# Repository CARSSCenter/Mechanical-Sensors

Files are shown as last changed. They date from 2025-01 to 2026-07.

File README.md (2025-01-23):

# Mechanical-Sensors
Sensors for mechanical biomarkers designed to interface with the OpenNerve platform

# About
The capacitive strain sensor is manufactured using silicone rubber and a novel wrinkled Parylene C process for increased gauge factor.


The temperature sensor is manufactured from gold on a polyimide thin-film substrate.


# Disclaimer
The contents of this repository are subject to revision. No representation or warranty, express or implied, is provided in relation to the accuracy, correctness, completeness, or reliability of the information, opinions, or conclusions expressed in this repository.

The contents of this repository (the “Materials”) are experimental in nature and should be used with prudence and appropriate caution. Any use is voluntary and at your own risk.

The Materials are made available “as is” by USC (the University of Southern California and its trustees, directors, officers, employees, faculty, students, agents, affiliated organizations and their insurance carriers, if any), its collaborators Med-Ally LLC and Medipace Inc., and any other contributors to this repository (collectively, “Providers”). Providers expressly disclaim all warranties, express or implied, arising in connection with the Materials, or arising out of a course of performance, dealing, or trade usage, including, without limitation, any warranties of title, noninfringement, merchantability, or fitness for a particular purpose.

Any user of the Materials agrees to forever indemnify, defend, and hold harmless Providers from and against, and to waive any and all claims against Providers for any and all claims, suits, demands, liability, loss or damage whatsoever, including attorneys' fees, whether direct or consequential, on account of any loss, injury, death or damage to any person or (including without limitation all agents and employees of Providers and all property owned by, leased to or used by either Providers) or on account of any loss or damages to business or reputations or privacy of any persons, arising in whole or in part in any way from use of the Materials or in any way connected therewith or in any way related thereto.

The Materials, any related materials, and all intellectual property therein, are owned by Providers.

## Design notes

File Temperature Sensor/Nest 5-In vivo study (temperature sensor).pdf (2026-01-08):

## In Vivo Study (Rat)

The temperature sensor and commercial reference were fixed to the left thigh muscle of the rat. We recorded 6 sets of data at intervals of about 1 min, and the results showed that the difference between the temperature sensor and the commercial reference was always within 0.2 °C. The resolution of our temperature sensor was within 0.05 °C, meanwhile, there was no obvious noise found when working in vivo. Therefore, experiments in vitro and in vivo have reached similar conclusions: the temperature sensor has the characteristics of high accuracy and high resolution. The temperature sensor is suitable for implantable tissue/organ temperature measurement for various applications.

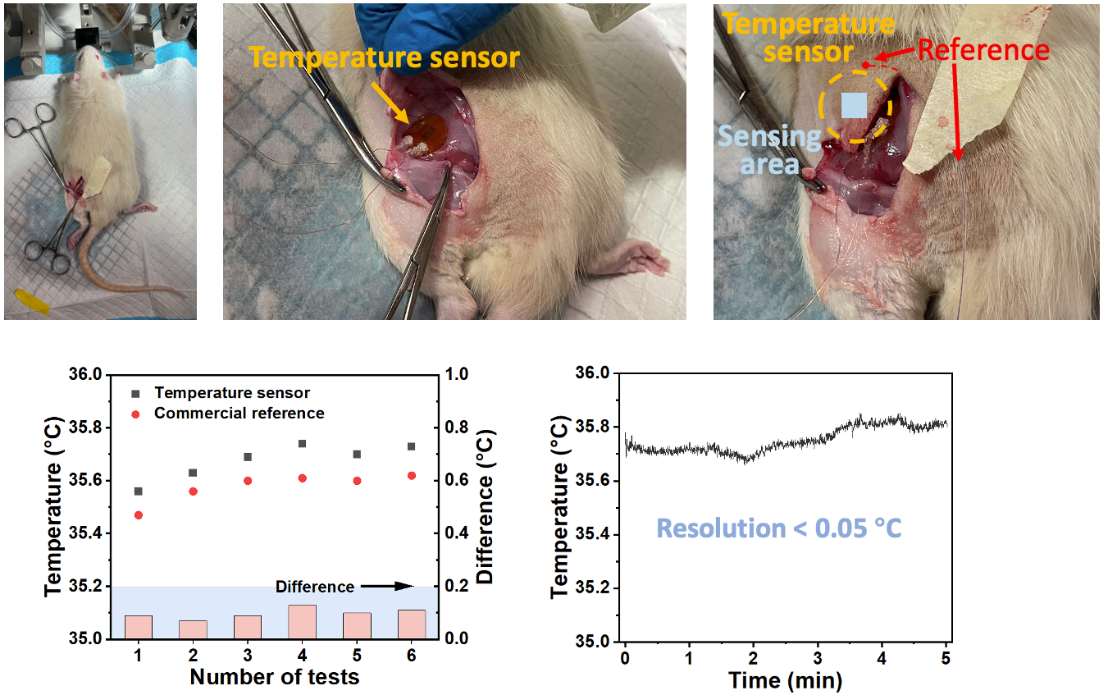
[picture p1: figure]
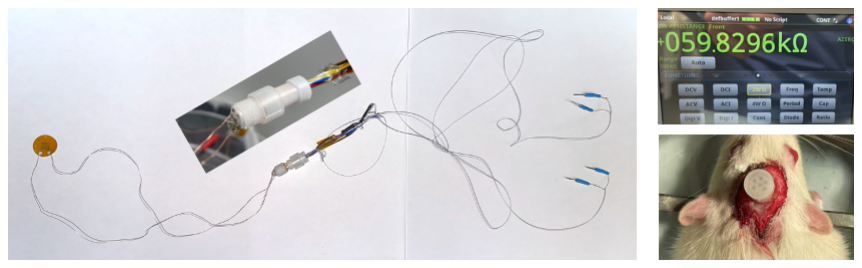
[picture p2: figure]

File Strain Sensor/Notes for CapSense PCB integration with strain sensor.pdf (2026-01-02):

# Stretchable capacitive strain sensor

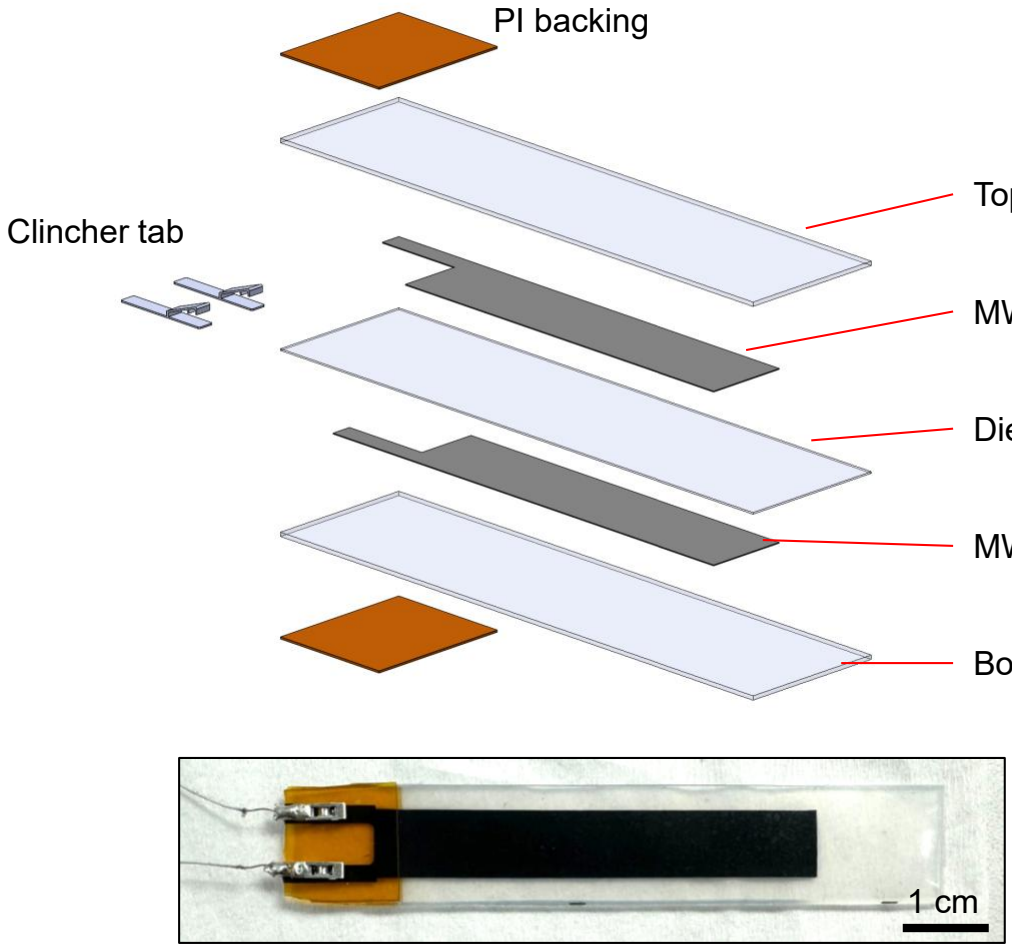
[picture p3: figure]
PI backing; Clincher tab

Custom strain sensor: spray-coated multiwall carbon nanotubes (MWCNTs) on Ecoflex

MWCNT

MWCNT

Top Ecoflex

Dielectric layer

Bottom Ecoflex

# Method 4: using single PI connector at the center of the sensor

Step 1: blade coat Ecoflex on a glass substrate. Next, spray coat the first CNT layer. Then, cover the contact pad with a film or tape. After that, blade coat the middle Ecoflex layer.

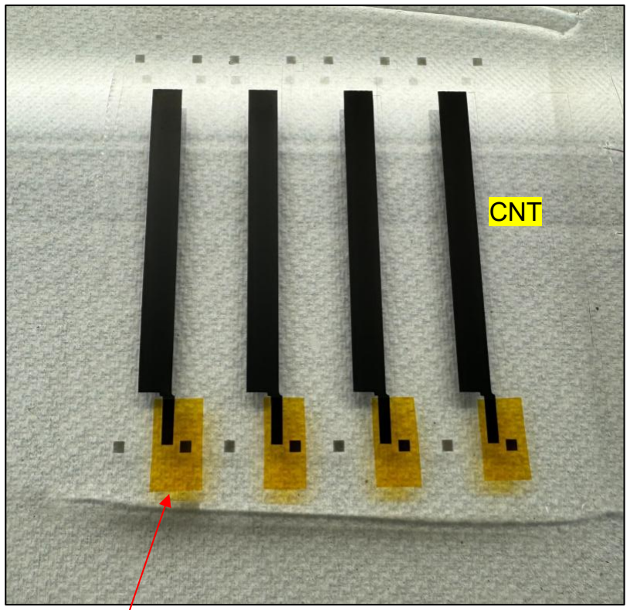
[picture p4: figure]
CNT
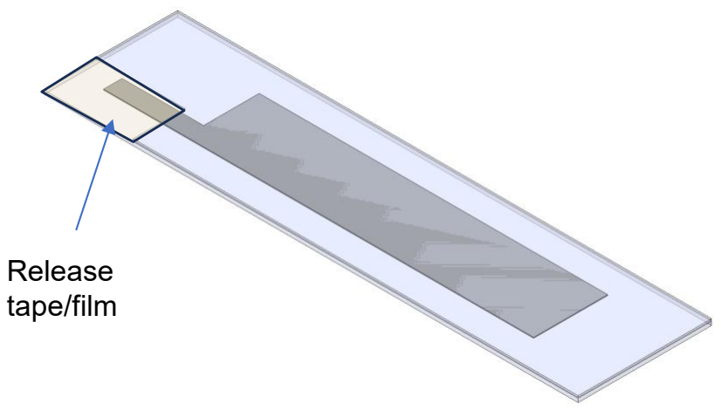
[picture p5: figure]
Release tape/film

Release
tape/film

# sensor

Step 2: remove the tape to expose the contact pad. Then, spray coat the second CNT Layer

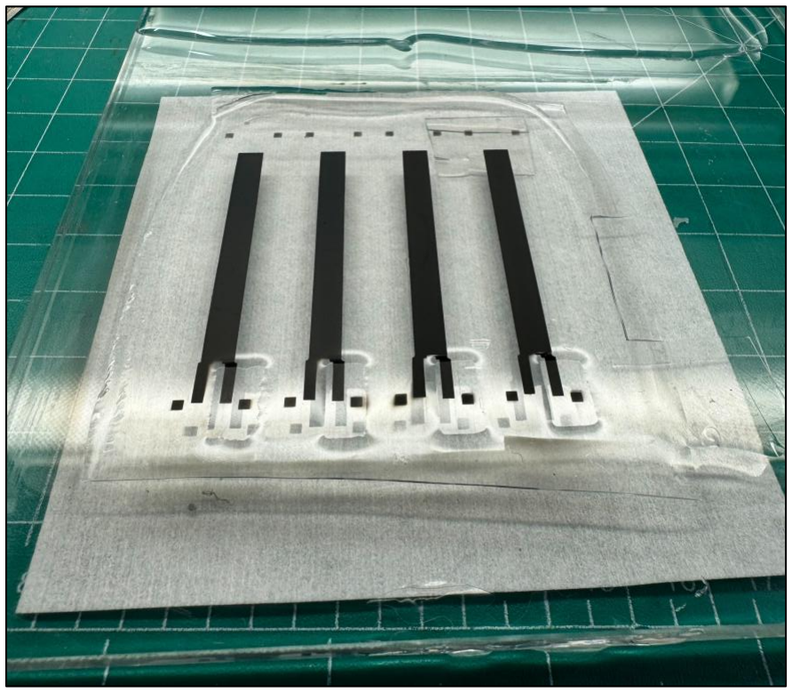
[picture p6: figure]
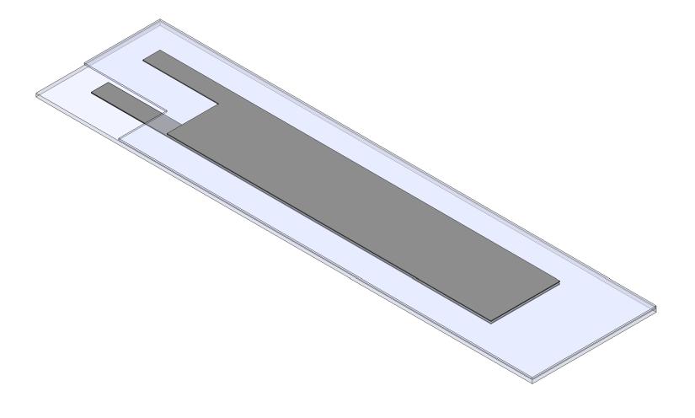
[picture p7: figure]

# sensor

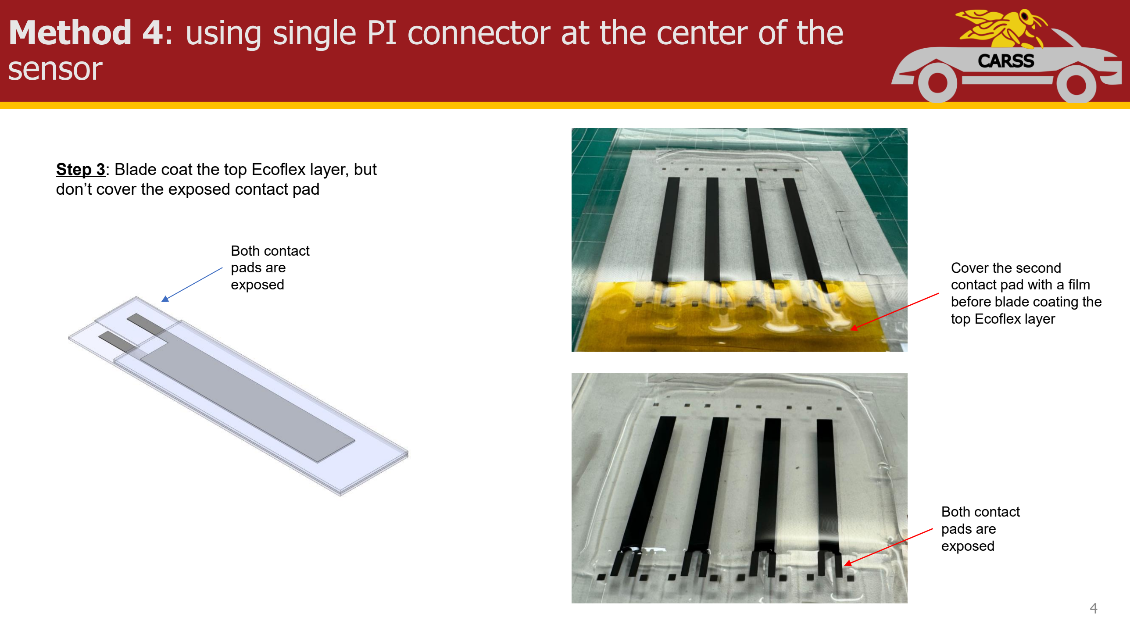
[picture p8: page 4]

Step 3: Blade coat the top Ecoflex layer, but don’t cover the exposed contact pad

Both contact
pads are
exposed

Both contact
pads are
exposed

Cover the second
contact pad with a film
before blade coating the
top Ecoflex layer

# sensor

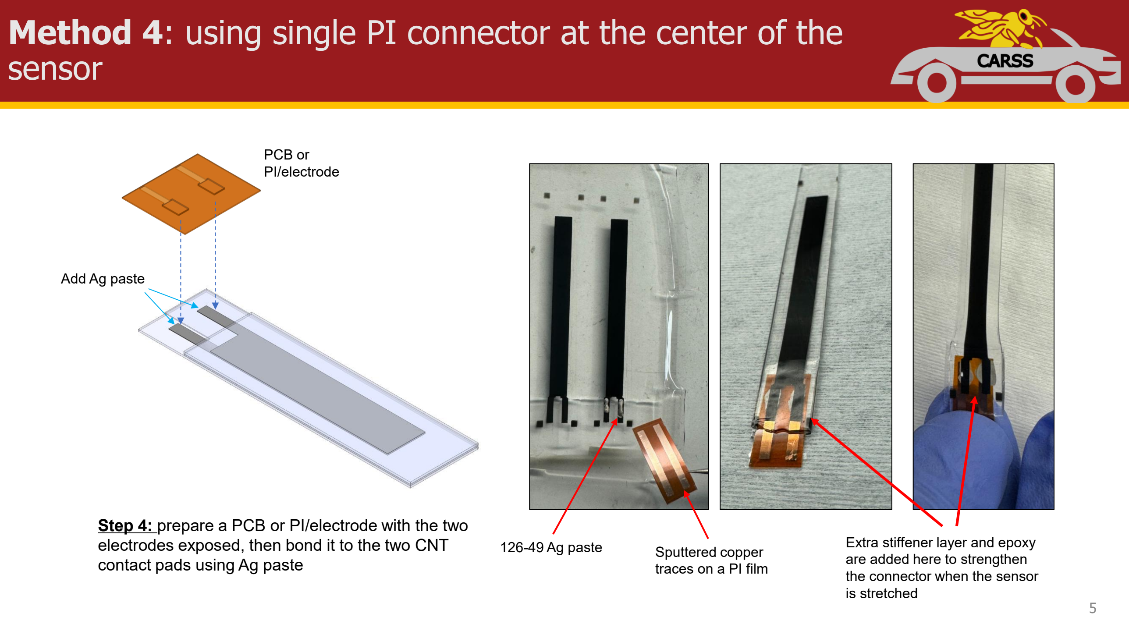
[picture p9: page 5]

Step 4: prepare a PCB or PI/electrode with the two electrodes exposed, then bond it to the two CNT contact pads using Ag paste

PCB or
PI/electrode

Add Ag paste

Extra stiffener layer and epoxy are added here to strengthen the connector when the sensor is stretched

126-49 Ag paste | Sputtered copper
| traces on a PI film

## Blue trace: sensor contour

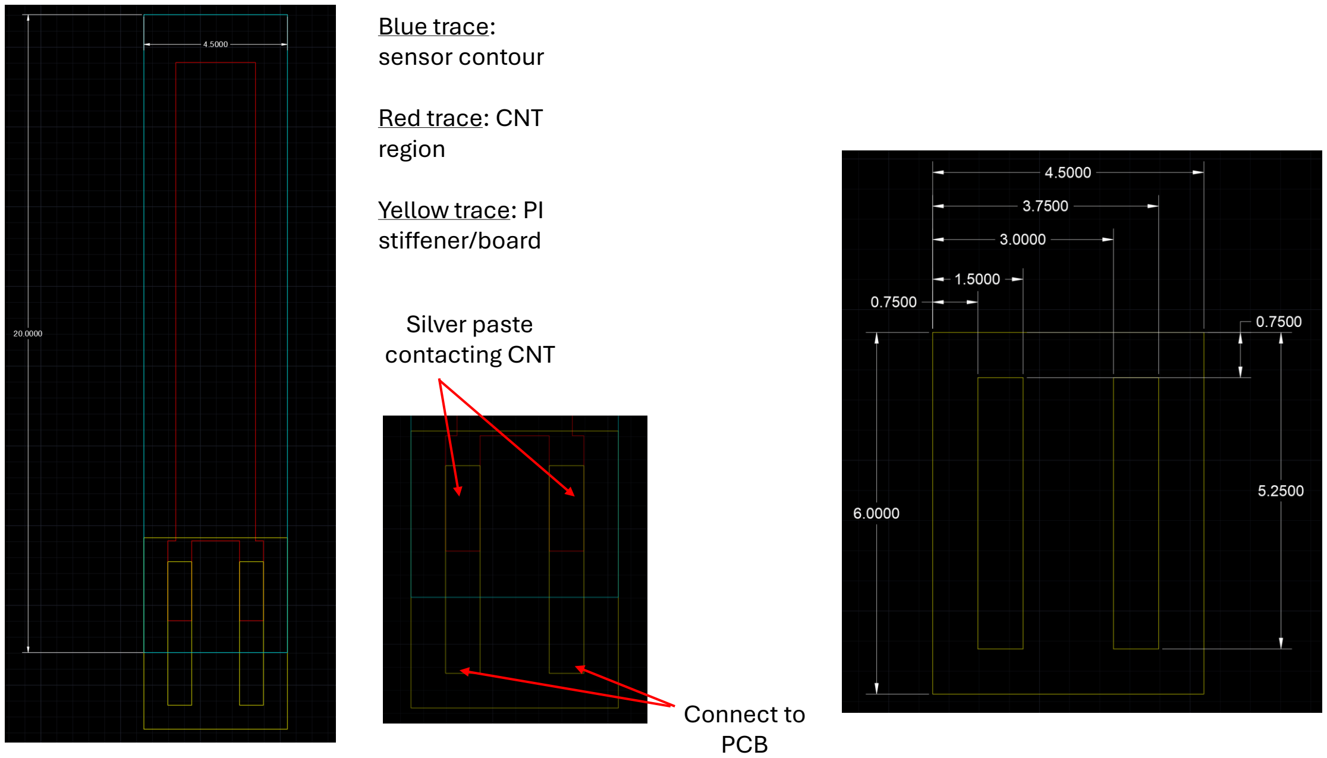
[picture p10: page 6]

## Red trace: CNT region

## Yellow trace: PI stiffener/board

## Silver paste contacting CNT

## Connect to PCB

# Sensor integrated with CapSense

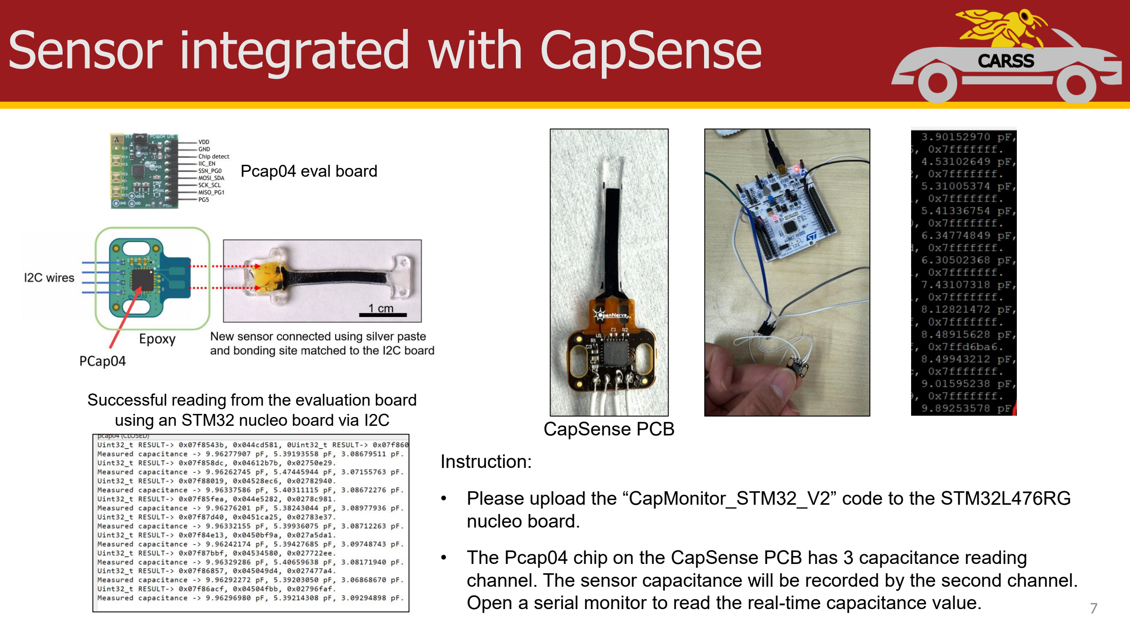
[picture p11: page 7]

Successful reading from the evaluation board using an STM32 nucleo board via I2C

Instruction:

- Please upload the “CapMonitor_STM32_V2” code to the STM32L476RG nucleo board.
- The Pcap04 chip on the CapSense PCB has 3 capacitance reading channel. The sensor capacitance will be recorded by the second channel. Open a serial monitor to read the real-time capacitance value.

Pcap04 eval board

CapSense PCB

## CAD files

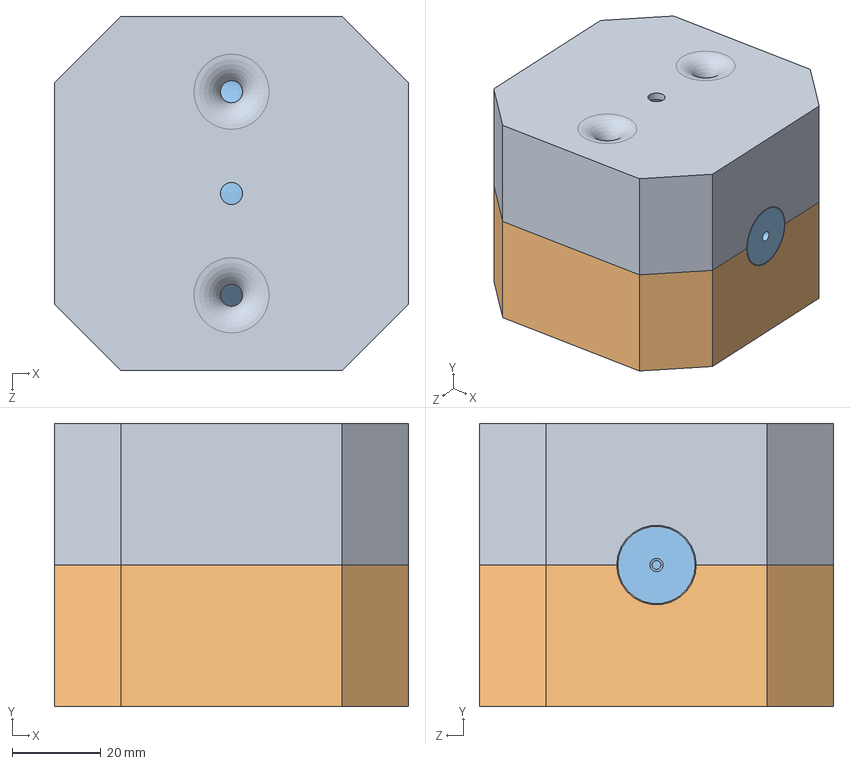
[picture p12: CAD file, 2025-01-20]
Strain Sensor/Bladder Ellipsoid_mold_v1/Ellipsoid_mold_v1.SLDASM
80.0 x 64.0 x 80.0 mm
sphere_mold_bottom_ellipsoidV2
ellipsoid v1
Ellipsoid_mold_top

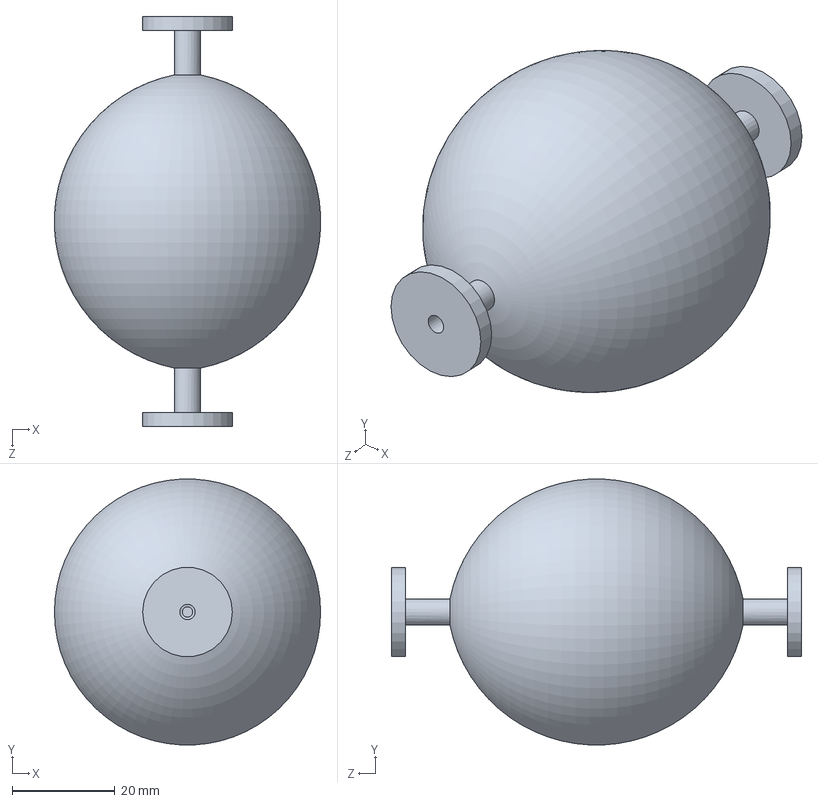
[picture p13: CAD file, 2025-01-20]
Strain Sensor/Bladder Ellipsoid_mold_v1/ellipsoid v1.SLDPRT
51.9 x 51.9 x 80.0 mm

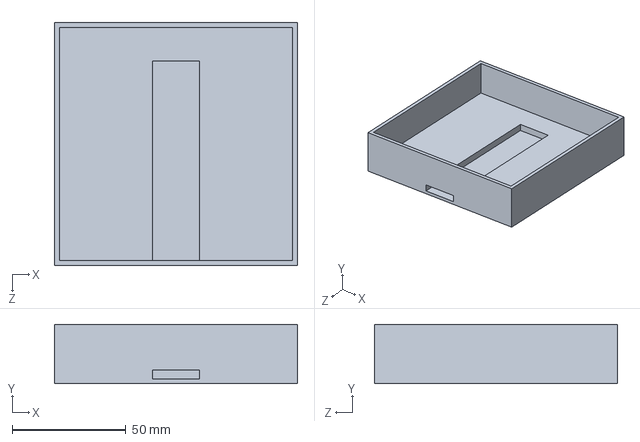
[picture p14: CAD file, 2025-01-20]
Strain Sensor/Strain Sensor Thermal accelerated aging setup design 3/HeaterV2_OutsideBase_4Glass_sq.SLDPRT
107.0 x 26.0 x 107.0 mm

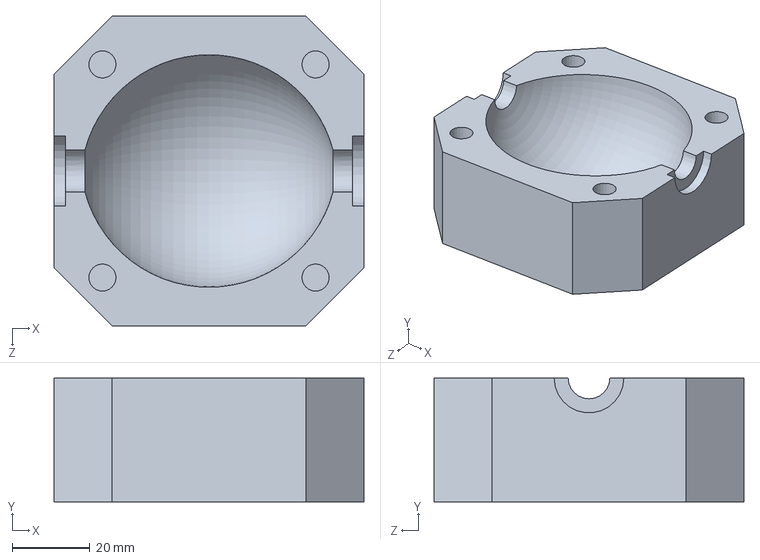
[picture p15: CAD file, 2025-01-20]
Strain Sensor/Bladder Ellipsoid_mold_v1/sphere_mold_bottom_ellipsoidV2.SLDPRT
80.0 x 32.0 x 80.0 mm

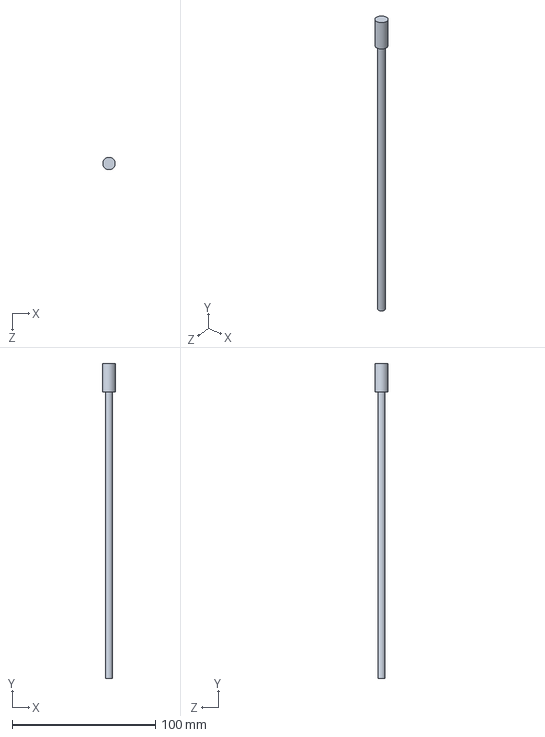
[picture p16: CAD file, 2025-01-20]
Strain Sensor/Strain Sensor Thermal accelerated aging setup design 3/thermal couple long.SLDPRT
8.75 x 220.0 x 8.75 mm

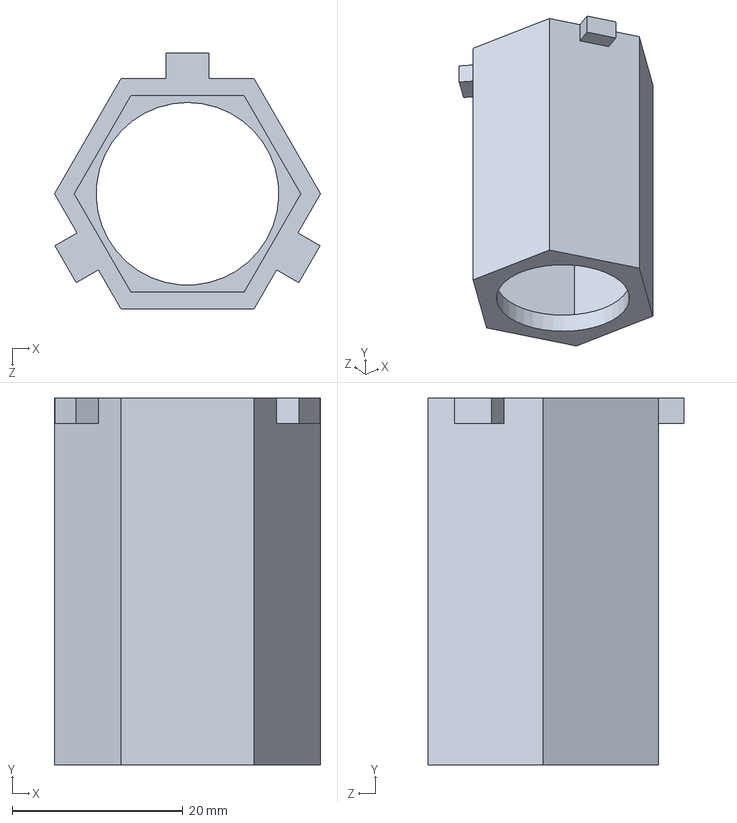
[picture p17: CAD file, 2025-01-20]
Strain Sensor/Strain Sensor Thermal accelerated aging setup design 3/heater tube adapter.SLDPRT
31.2 x 43.0 x 30.0 mm

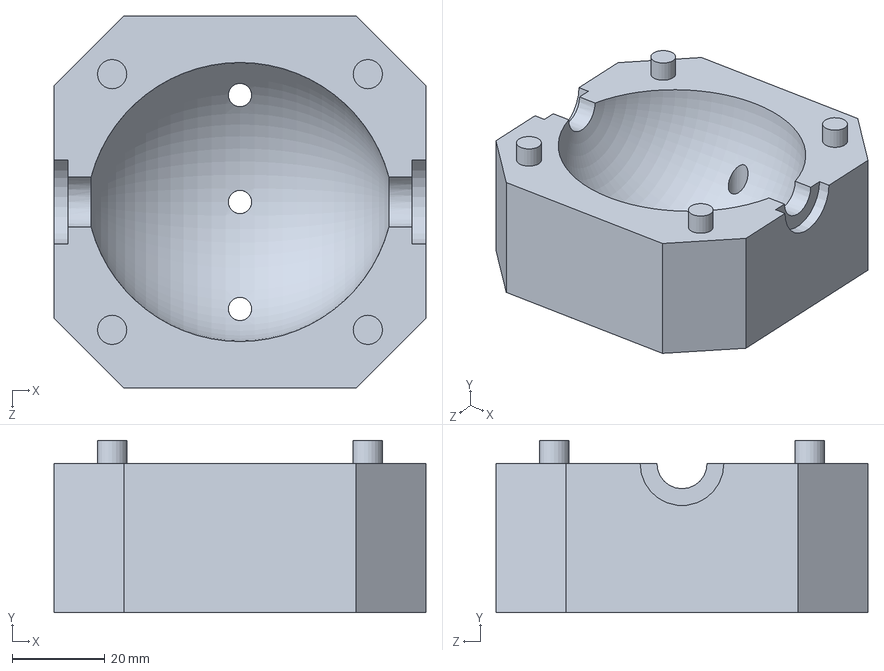
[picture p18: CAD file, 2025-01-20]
Strain Sensor/Bladder Ellipsoid_mold_v1/Ellipsoid_mold_top.SLDPRT
80.0 x 37.0 x 80.0 mm

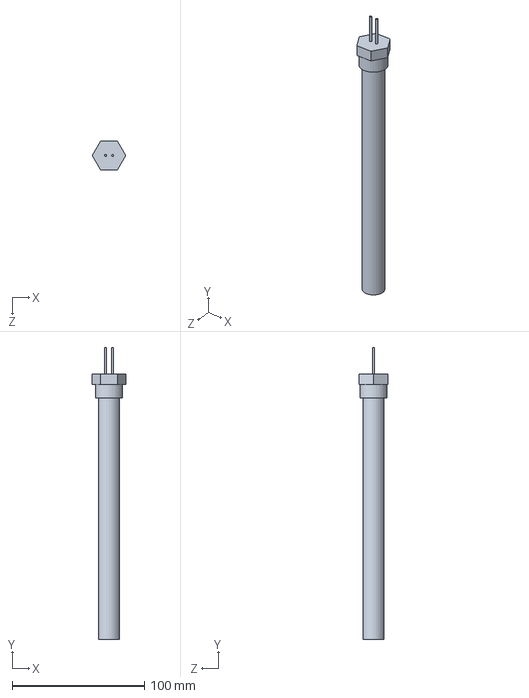
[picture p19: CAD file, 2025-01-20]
Strain Sensor/Strain Sensor Thermal accelerated aging setup design 3/heat rod.SLDPRT
25.4 x 221.0 x 22.0 mm

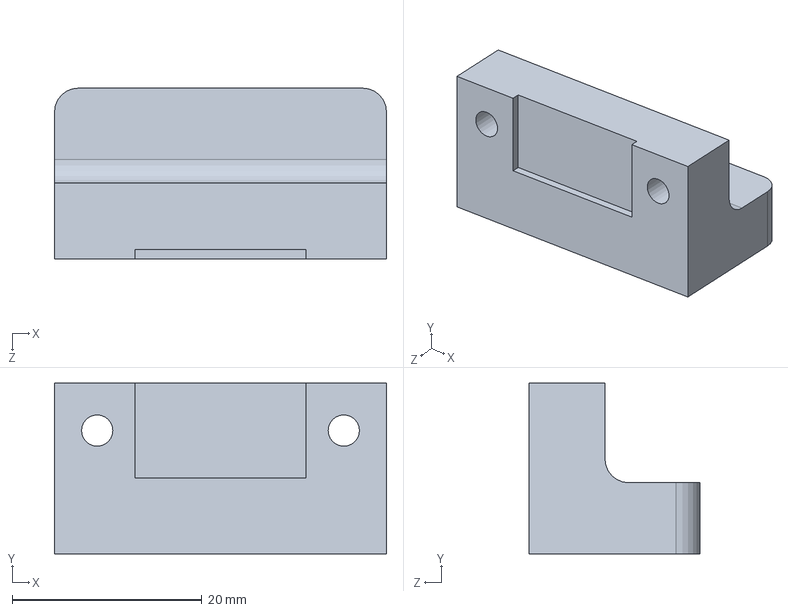
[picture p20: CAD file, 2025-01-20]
Strain Sensor/Strain Sensor Thermal accelerated aging setup design 3/HeaterV3_SensorBotClamp_V2.SLDPRT
35.0 x 18.0 x 18.0 mm

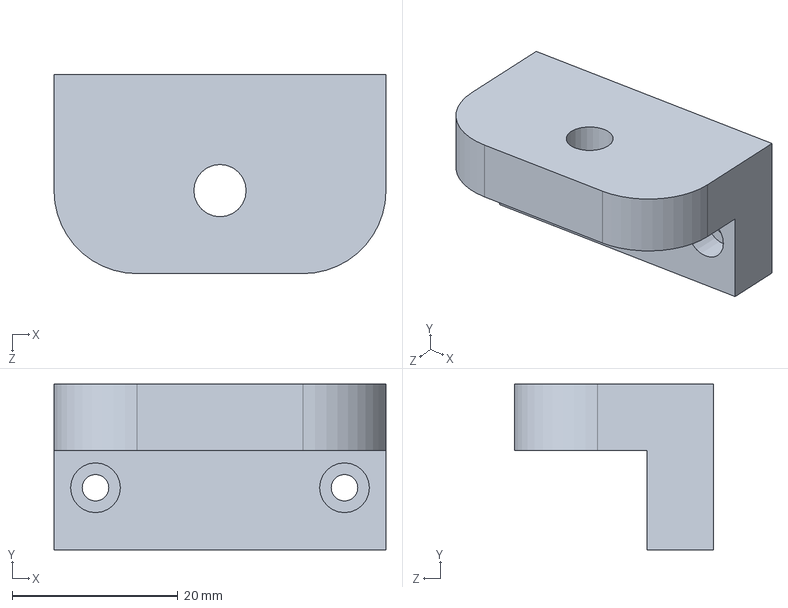
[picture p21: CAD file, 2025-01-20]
Strain Sensor/Strain Sensor Thermal accelerated aging setup design 3/HeaterV3_SensorTopClamp.SLDPRT
40.0 x 20.0 x 24.0 mm

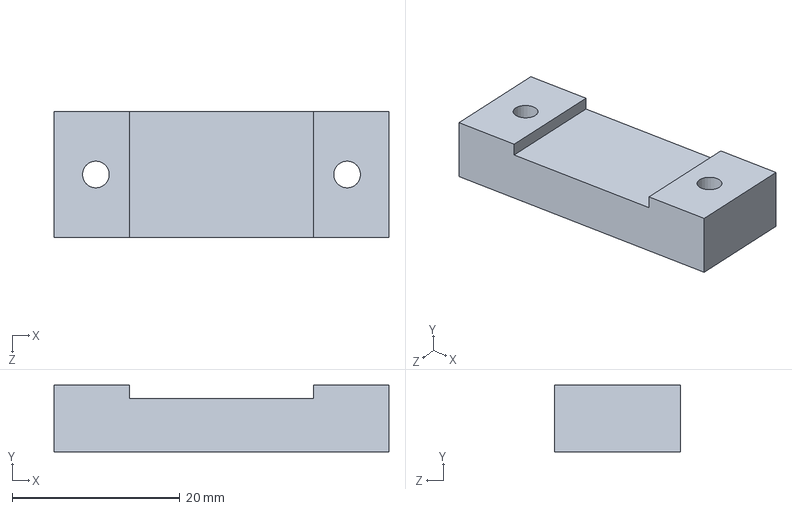
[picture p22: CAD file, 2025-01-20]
Strain Sensor/Strain Sensor Thermal accelerated aging setup design 3/holder_part_4_v3.SLDPRT
40.0 x 8.00 x 15.0 mm

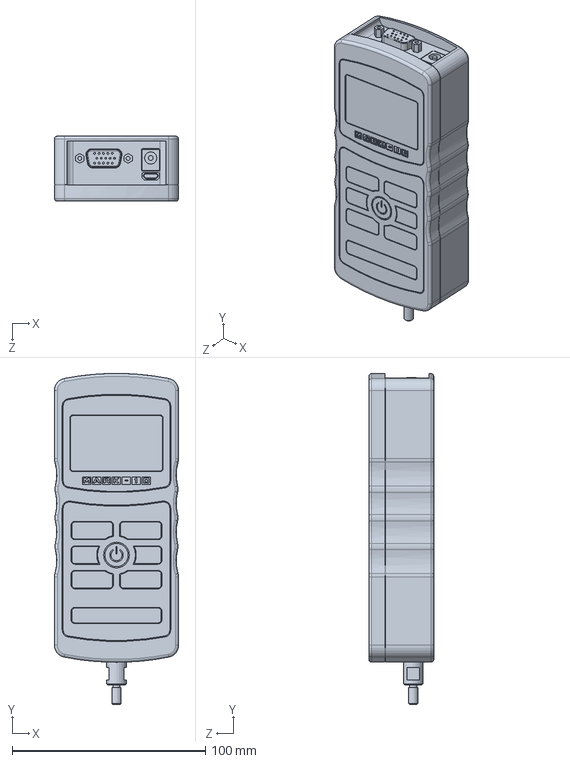
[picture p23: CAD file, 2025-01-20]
Strain Sensor/Strain Sensor Thermal accelerated aging setup design 3/M7 Series 7 Force Gauge.SLDPRT
64.3 x 171.1 x 33.8 mm

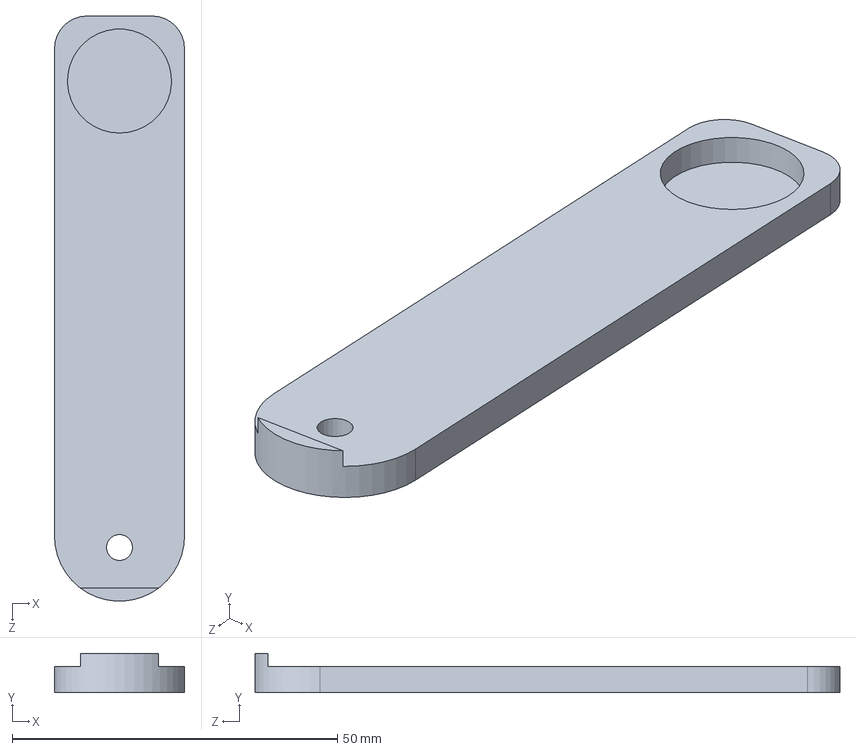
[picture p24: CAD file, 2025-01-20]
Strain Sensor/Strain Sensor Thermal accelerated aging setup design 3/HeaterV3_OutsideBaseTab_4Glass.SLDPRT
20.0 x 6.00 x 90.0 mm

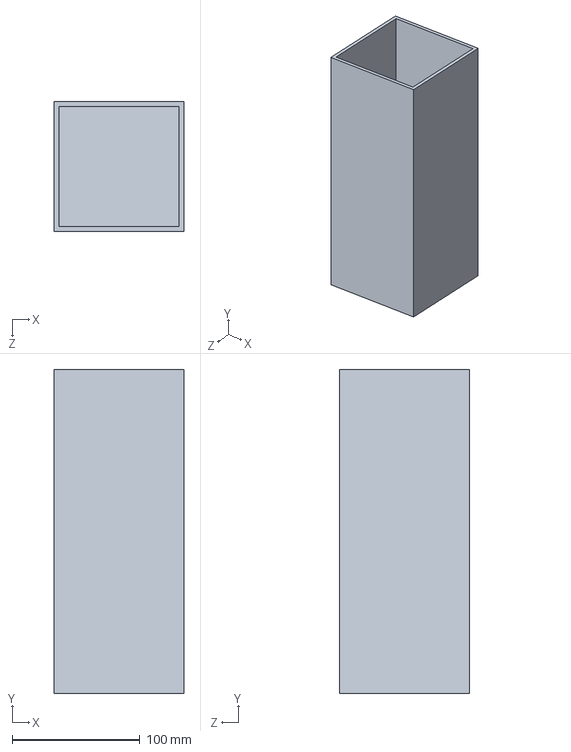
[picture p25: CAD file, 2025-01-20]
Strain Sensor/Strain Sensor Thermal accelerated aging setup design 3/Acrylic rectangular tank.SLDPRT
101.5 x 253.6 x 101.5 mm

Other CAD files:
Strain Sensor/2cm parallel plate sensor for sheep study 2.dwg
Temperature Sensor/Nest 5-Temp sensor mask design.dwg
Strain Sensor/NEST 5 Strain Sensor Mask CAD File.dwg
Strain Sensor/Strain Sensor Thermal accelerated aging setup design 3/TopCapHolder_Sq.SLDPRT
Strain Sensor/Strain Sensor Thermal accelerated aging setup design 3/90111A332_316 Stainless Steel Coupling Nut.SLDPRT
Strain Sensor/Strain Sensor Thermal accelerated aging setup design 3/91828A251_18-8 Stainless Steel Hex Nut.SLDPRT
Strain Sensor/Strain Sensor Thermal accelerated aging setup design 3/98434A727_18-8 Stainless Steel Female Hex Thread Adapter.SLDPRT
Strain Sensor/Strain Sensor Thermal accelerated aging setup design 3/98863A542_Super-Corrosion-Resistant 316 Stainless Steel Threaded Rod.SLDPRT
Strain Sensor/Strain Sensor Thermal accelerated aging setup design 3/ESM303 MARKETING MODEL.stp
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

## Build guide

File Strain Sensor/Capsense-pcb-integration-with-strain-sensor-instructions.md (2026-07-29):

# Stretchable Capacitive Strain Sensor

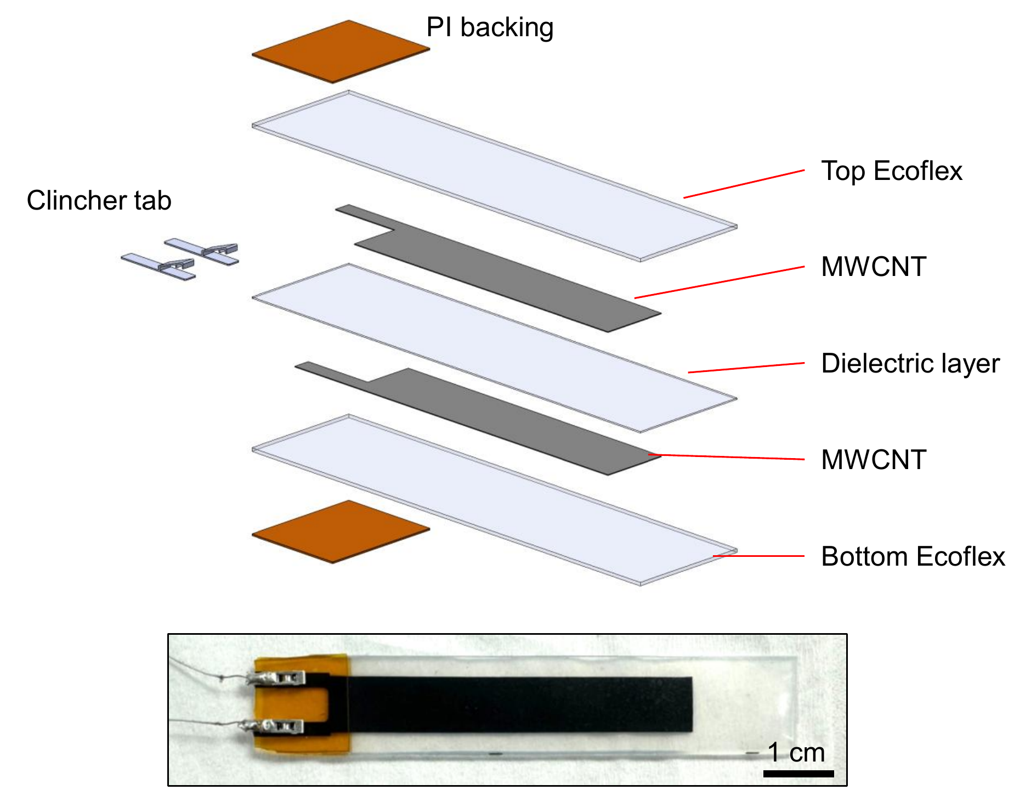
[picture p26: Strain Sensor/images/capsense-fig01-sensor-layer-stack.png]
Exploded layer stack of the strain sensor (PI backing, top Ecoflex, MWCNT, dielectric layer, MWCNT, bottom Ecoflex, clincher tab) and a photo of the finished sensor with a 1 cm scale bar


*Custom strain sensor: spray-coated multiwall carbon nanotubes (MWCNTs) on Ecoflex*

## Using Single PI Connector at the Center of the Sensor

**Step 1**: blade coat Ecoflex on a glass substrate. Next, spray coat the first CNT layer. Then, cover the contact pad with a film or tape. After that, blade coat the middle Ecoflex layer.

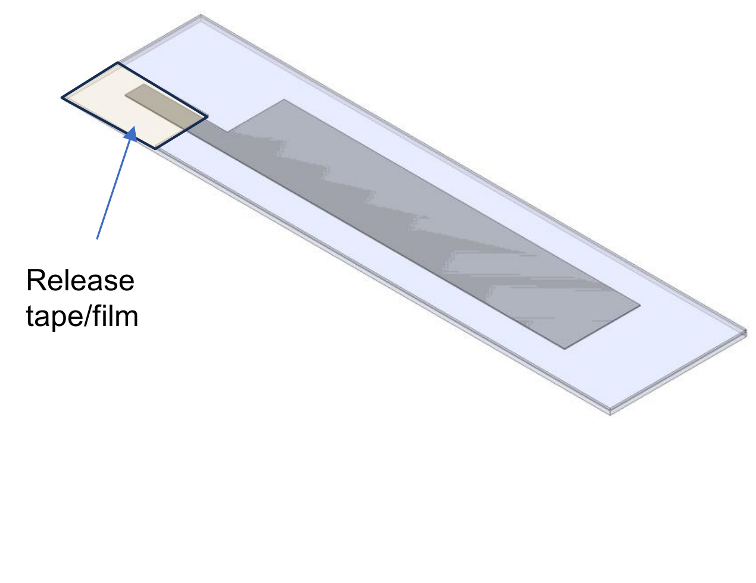
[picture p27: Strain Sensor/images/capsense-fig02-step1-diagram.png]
Schematic of the release tape/film placed over the contact pad before the middle Ecoflex layer is coated


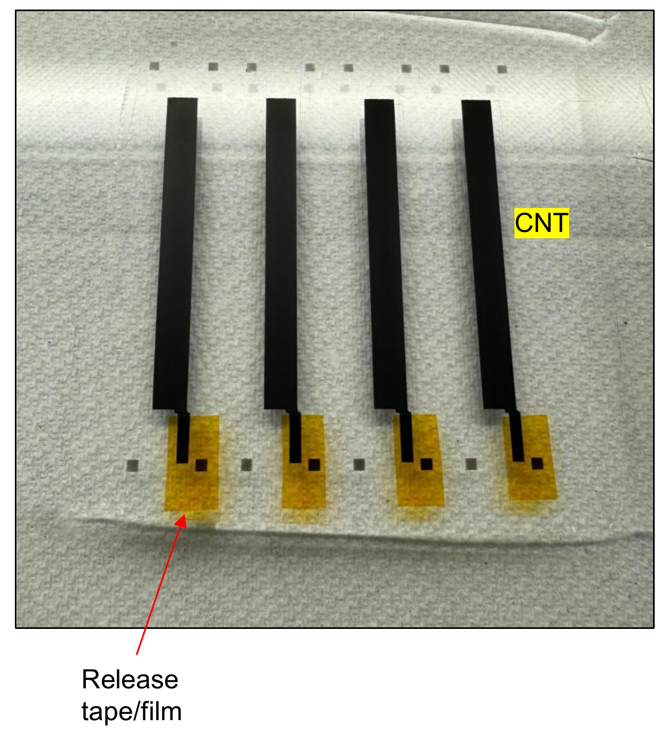
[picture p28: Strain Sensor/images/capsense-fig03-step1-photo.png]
Photo of four spray-coated CNT strips on fabric, with the release tape/film over each contact pad highlighted


**Step 2**: remove the tape to expose the contact pad. Then, spray coat the second CNT Layer.

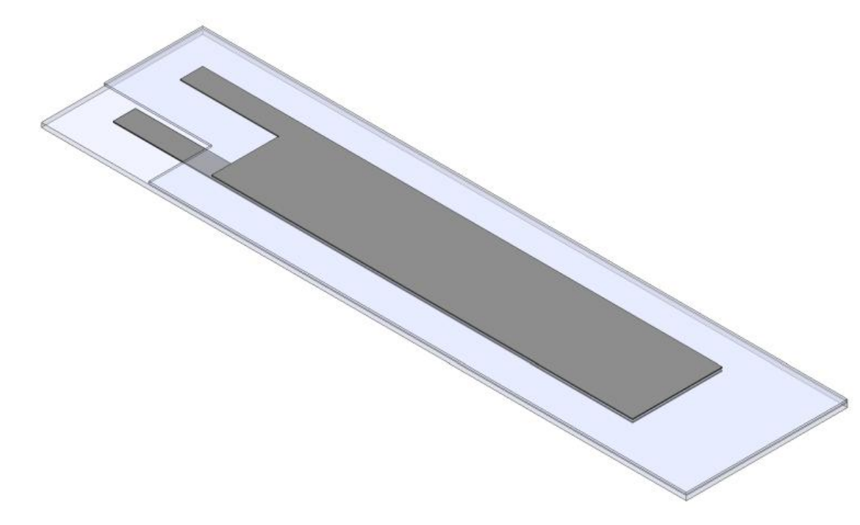
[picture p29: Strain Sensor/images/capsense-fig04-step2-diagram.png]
Schematic showing the contact pad exposed after removing the release tape


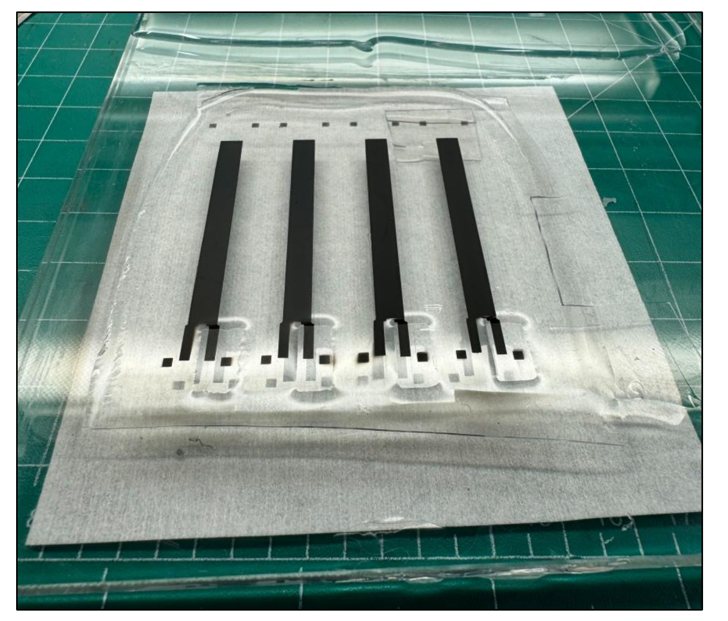
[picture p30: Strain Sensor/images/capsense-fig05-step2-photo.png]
Photo of the sensor strips after the second CNT spray coat, laid out on a cutting mat


**Step 3**: Blade coat the top Ecoflex layer, but don't cover the exposed contact pad.

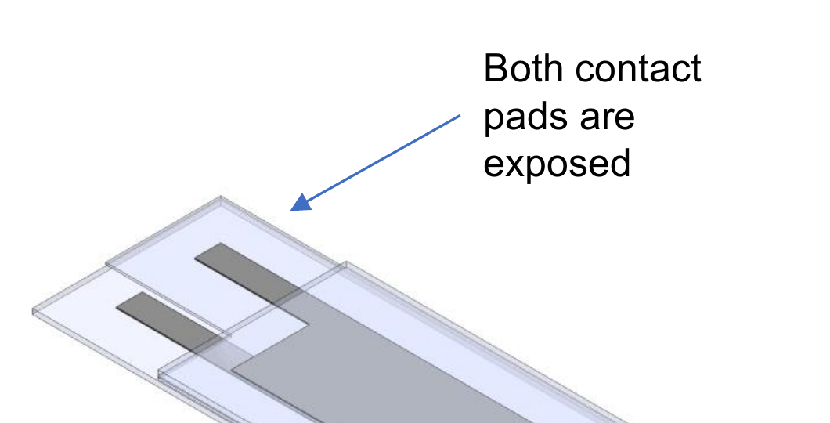
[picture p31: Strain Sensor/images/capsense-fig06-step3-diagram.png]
Schematic indicating that both contact pads remain exposed after the top Ecoflex coat


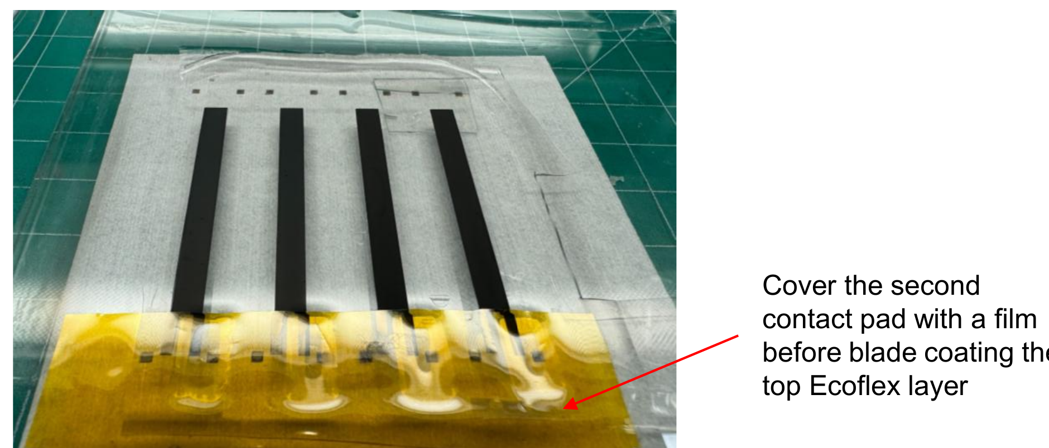
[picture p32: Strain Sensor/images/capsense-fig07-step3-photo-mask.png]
Photo of the sensor strips with the top Ecoflex mask in place, showing where the second contact pad should be covered with film before coating


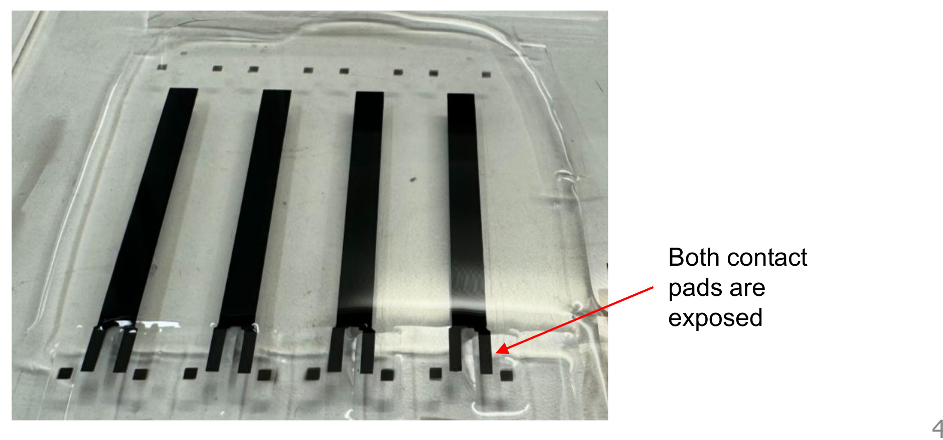
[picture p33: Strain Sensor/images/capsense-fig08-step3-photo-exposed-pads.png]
Photo of the finished strips with both contact pads exposed after the top Ecoflex coat


**Step 4:** prepare a PCB or PI/electrode with the two electrodes exposed, then bond it to the two CNT contact pads using Ag paste.

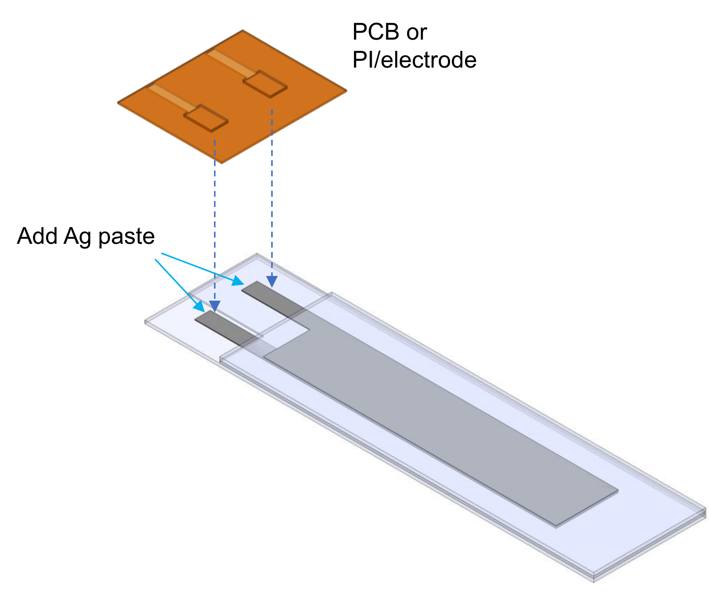
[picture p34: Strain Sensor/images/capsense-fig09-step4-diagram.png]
Schematic of the PCB/PI electrode being bonded to the two CNT contact pads with Ag paste


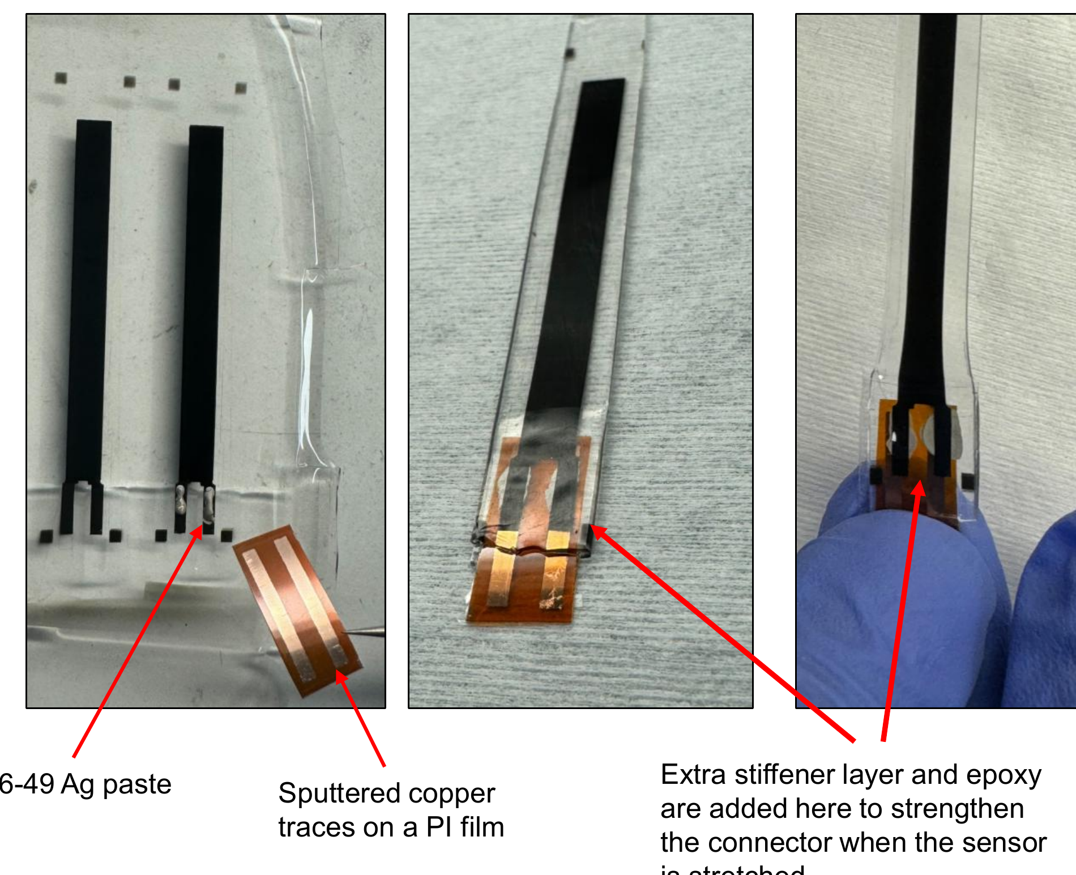
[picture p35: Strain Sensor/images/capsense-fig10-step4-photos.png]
Three photos showing the 126-49 Ag paste bond, the sputtered copper traces on a PI film, and the extra stiffener layer/epoxy added to strengthen the connector when the sensor is stretched


## CAD Outline and Dimensions Reference

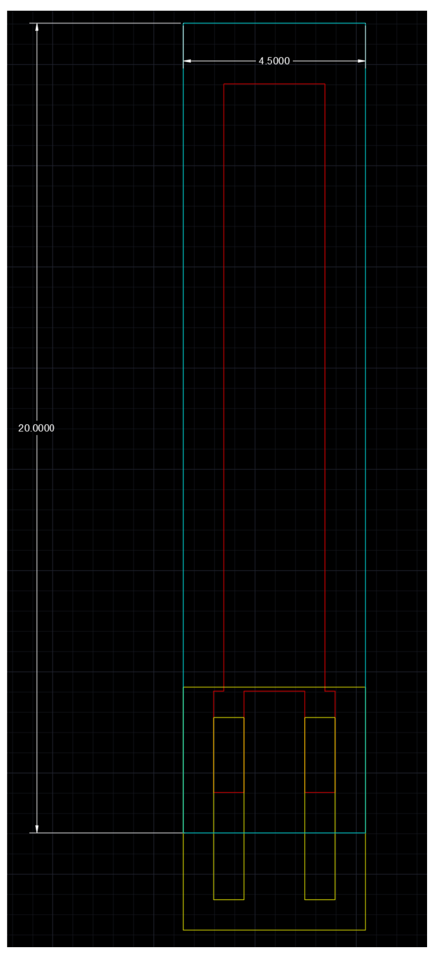
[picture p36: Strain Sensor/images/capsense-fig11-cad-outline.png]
Full CAD outline of the sensor: cyan trace is the sensor contour, red trace is the CNT region, yellow trace is the PI stiffener/board, dimensioned at 20.0000 x 4.5000


- **Blue trace:** sensor contour
- **Red trace:** CNT region
- **Yellow trace:** PI stiffener/board

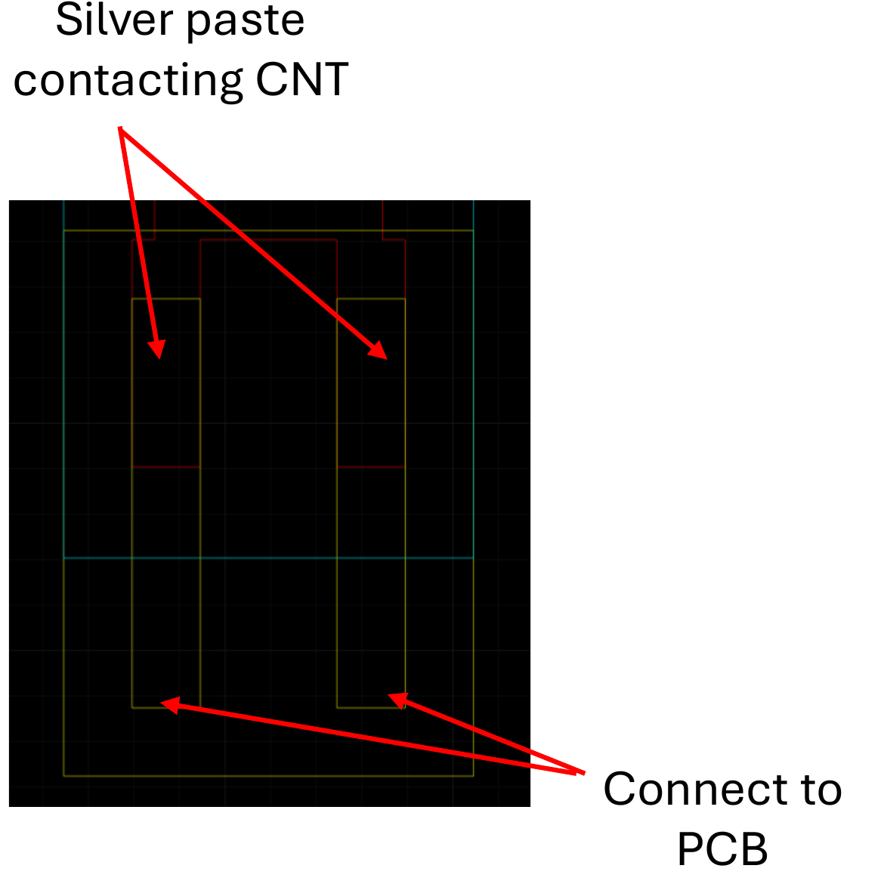
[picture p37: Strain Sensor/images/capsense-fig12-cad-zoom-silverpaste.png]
Zoomed CAD view of the two contact pads, with arrows marking where silver paste contacts the CNT and where the connector attaches to the PCB


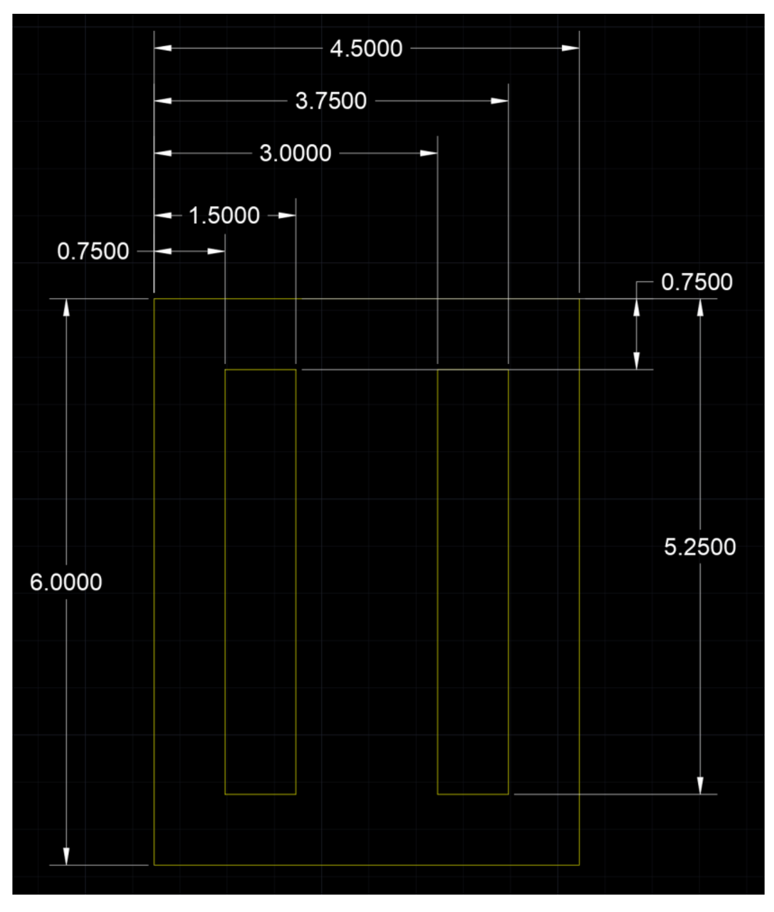
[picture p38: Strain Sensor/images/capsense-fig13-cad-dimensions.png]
Dimensioned CAD drawing of the PI stiffener/board footprint (6.0000 x 4.5000 overall, with 0.7500-3.7500-1.5000 pad spacing)


## Sensor Integrated with CapSense

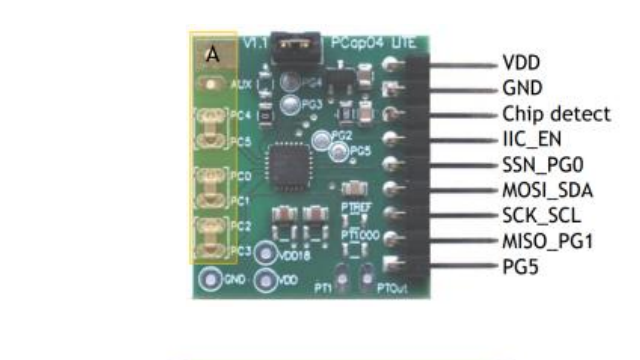
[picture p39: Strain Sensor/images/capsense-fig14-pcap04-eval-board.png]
Pcap04 eval board with pin labels: VDD, GND, Chip detect, IIC_EN, SSN_PG0, MOSI_SDA, SCK_SCL, MISO_PG1, PG5


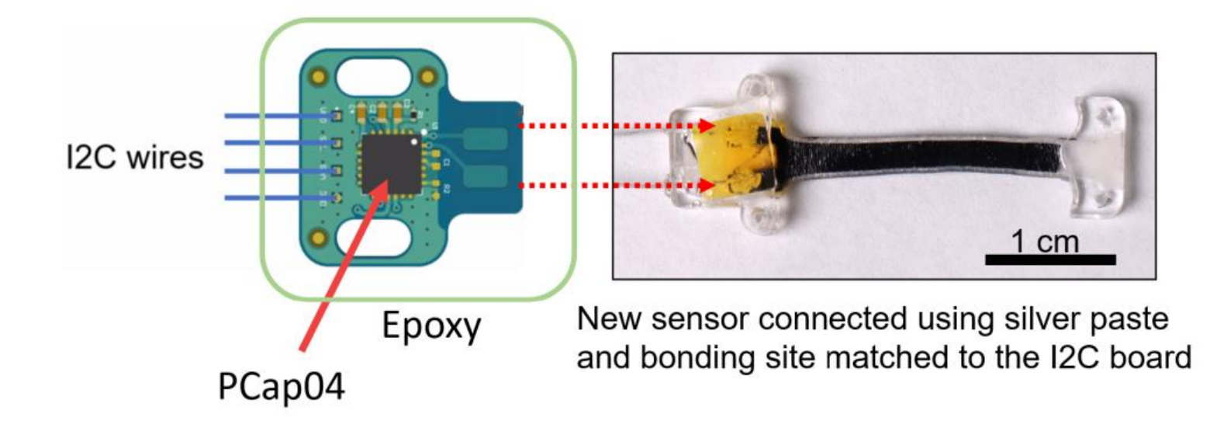
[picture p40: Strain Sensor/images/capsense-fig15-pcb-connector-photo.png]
The CapSense PCB (I2C wires, PCap04 chip, epoxy strain relief) connected to the strain sensor via silver paste, with a 1 cm scale bar


Successful reading from the evaluation board using an STM32 nucleo board via I2C.

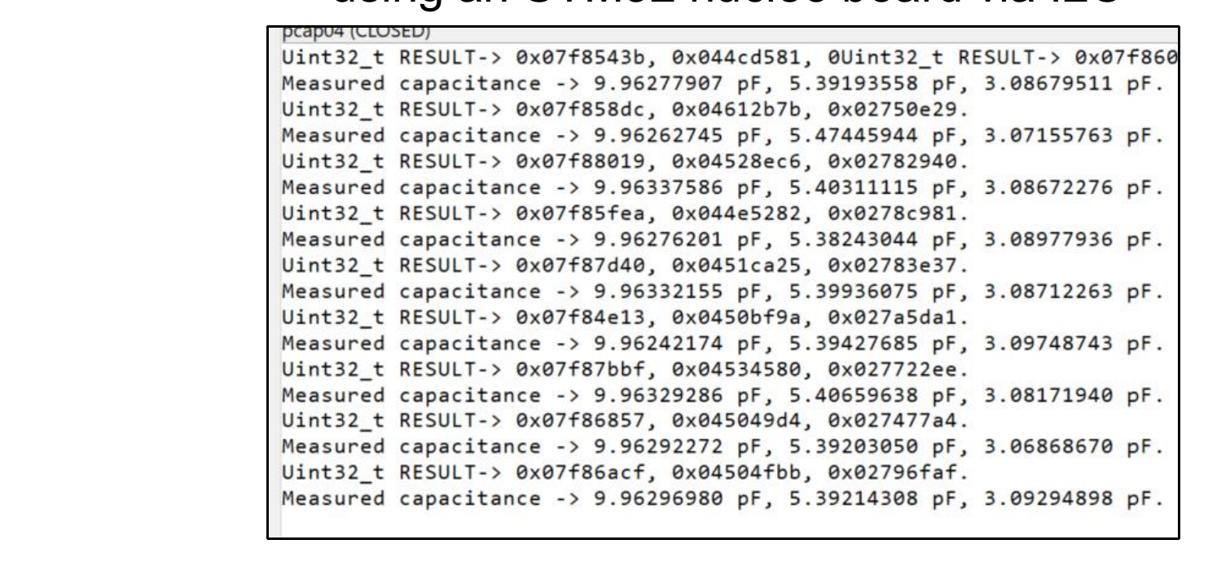
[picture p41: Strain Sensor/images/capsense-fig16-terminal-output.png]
Terminal screenshot of the Pcap04 evaluation board output, showing repeated measured capacitance readings in pF


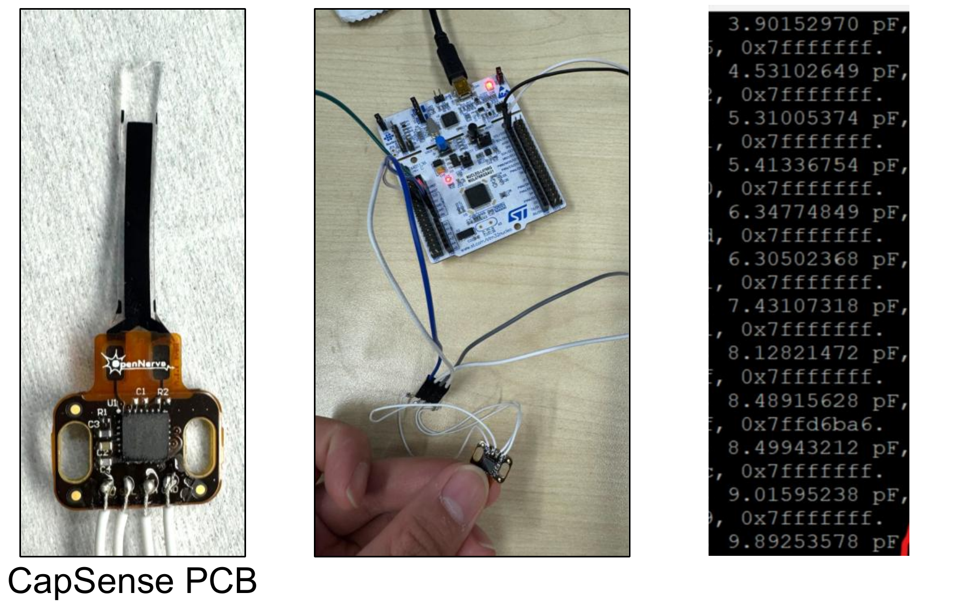
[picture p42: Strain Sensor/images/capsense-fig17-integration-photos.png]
Photos of the CapSense PCB, the wired STM32 nucleo board setup, and a terminal window streaming real-time capacitance readings


**Instruction:**

- Please upload the "CapMonitor_STM32_V2" code to the STM32L476RG nucleo board.
- The Pcap04 chip on the CapSense PCB has 3 capacitance reading channels. The sensor capacitance will be recorded by the second channel. Open a serial monitor to read the real-time capacitance value.

---

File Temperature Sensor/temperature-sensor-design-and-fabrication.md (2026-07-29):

# NEST 5 – Temperature Sensor Design and Fabrication

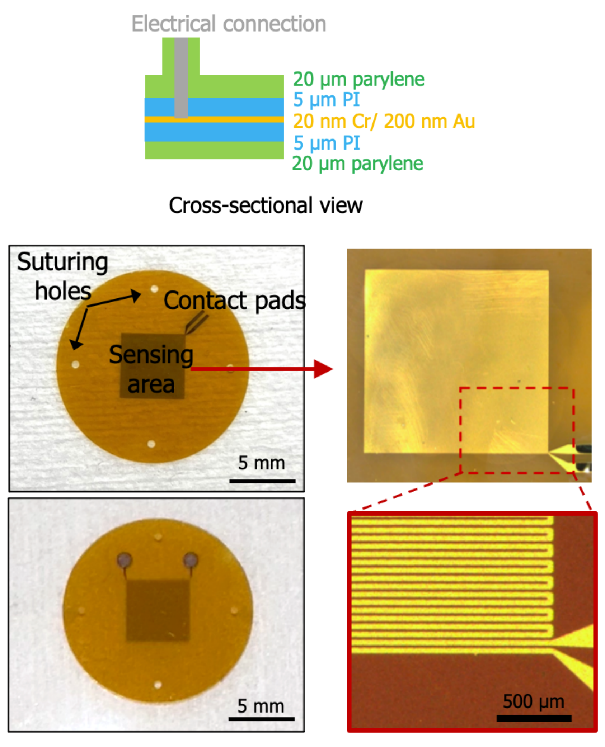
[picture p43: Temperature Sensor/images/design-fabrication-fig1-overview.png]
Sensor overview: layer cross-section, suturing holes, contact pads, sensing area, and progressively zoomed micrographs of the interdigitated sensing electrodes


## NEST 5 – Temperature Sensor Fabrication Protocol

## 1. Deposit the Sacrificial Layer and Base Polyimide

### 1.1 Sputtering Copper as Sacrificial Layer

*Materials:* 4” prime silicon wafer(s)

*Note: Before sputtering, silicon wafers must be cleaned with acetone and IPA.*

*Equipment:* KJL Sputter

The sputtering time is 1800s, Sputter Deposition Rate is 150 Å/min. The thickness of copper is about 150 nm.

### 1.2 Polyimide Deposition of the Base Layer

*Materials:* Polyimide: PI2545 Monomer

*Equipment:* Hot plate and Vacuum Heating Chamber

1. First, the PI2545 monomer is removed from the refrigerator and placed at room temperature for half an hour to ambient temperature, and the whole process is operated in a clean room.
2. A 5 μm PI layer was prepared using a spin coating operation. In detail, about 10 ml of PI monomer was poured onto the center of the silicon wafer, and the spin coating was controlled at 1100 rpm with an acceleration of 500 for 30 s. Subsequently, it was treated at 110 °C for 2 min and at 150 °C for 3 min. Finally, it was transferred to a vacuum-heated chamber at 260 °C for 1 hour. Cool down all night.

## 2. Deposit and Pattern Metal

### 2.1 Deposition, Exposure, and Development of Photoresist

*Note: The Polyimide surface needs to be cleaned with acetone and IPA.*

*Materials:* AZ nLOF 2035 resist

*Equipment:* Hot plate and Mask aligner (MAB6)

1. Metal patterns are defined using the Lift-off process. Spin coat AZ nLOF 2035 resist (negative) at 4000 rpm (~3 µm) for 60 s, and bake at 110 °C for 60 s.
2. Expose (365 nm) using a dose of 80 mJ/cm².
3. Post-bake at 110 °C for 60 s.
4. Develop using AZ 917 MIF for about 60 s, then check patterned PR using a microscope.
   - *Note: If the photoresist thickness is not within the range of 3-4 µm, the speed must be recalibrated. The photoresist thickness can be measured after development is complete. If the photoresist is not applied correctly (e.g., if there is not enough photoresist used to cover the entire wafer or if a particle is stuck on the surface), remove the photoresist and return to step 2.1.*

### 2.2 Deposit Metals

*Materials:* Titanium and Platinum

*Equipment:* CHA E-beam evaporator

1. Deposit the metal stack up (20 nm Cr (adhesion layer) + 200 nm Au) at 1 Å/s.
   - *Note: Wait 30 minutes between different types of metal to allow the crucible to cool down.*
   - *Note: Pause for 30 minutes after each 50 nm of gold (i.e. deposit in three 50 nm runs with 30 min pauses between each run).*

### 2.3 Pattern Metal via Lift-off

*Materials:* NMP rinse and Acetone

*Equipment:* Glass dishes designated for liftoff, Sonicating bath, and Stereoscope

*Note: All steps (2.3) are performed one wafer at a time; repeat the following procedure once for each wafer.*

1. Hold the NMP bath (with the wafer inside) above the sonicating bath and intermittently touch the water surface for intermittent sonication until the metal appears to be fully lifted off.
2. Once the liftoff appears to be complete, move the NMP bath back to the hot plate and transfer the wafer to a room-temperature NMP bath for more than 5 minutes.
   - Do not allow the wafer to dry, as this will cause the lifted-off metal to permanently stick to the wafer surface.
3. Lift the wafer out of the room temperature NMP bath, rinse it with NMP using a squeeze bottle, and move it to an IPA bath for more than 5 minutes.
   - Do not allow the wafer to dry, as this will cause the lifted-off metal to permanently stick to the wafer surface.
4. Inspect the wafer for any remaining metal while submerged in acetone under a stereoscope.
   - If any undesired metal remains (metal that has not yet been lifted off or metal flakes sitting on the surface), move the wafer back to the warm NMP bath and repeat the process from step 2.3.1.
   - If any stubborn metal remains after repeating sonication, a foam swab can be used to gently dislodge the metal from the wafer surface.
5. Lift the wafer out of the acetone bath, rinse it with acetone using a squeeze bottle, and move it to a DI water bath for more than 3 minutes.
   - Do not allow the wafer to dry, as this will cause the lifted-off metal to permanently stick to the wafer surface.
6. Re-inspect the wafer for any remaining metal while submerged in water under the stereoscope.
   - If any undesired metal remains (metal that has not yet been lifted off or metal flakes sitting on the surface), move the wafer back to the warm NMP bath and repeat the process from step 2.3.1.
7. Rinse the wafer with DI water three times and blow-dry it with N₂.
8. Inspect the metal features under a microscope and return to step 2.3.1 if any metal or photoresist remains.

## 3. Deposit Top Polyimide

*Materials:* Polyimide: PI2545 Monomer

*Equipment:* Hot plate and Vacuum Heating Chamber

1. First, the PI2545 monomer is removed from the refrigerator and placed at room temperature for half an hour to reach ambient temperature. The entire process is operated in a clean room.
2. A 5 μm PI layer was prepared using a spin coating operation. In detail, approximately 10 ml of PI monomer was poured onto the center of the silicon wafer, and the spin coating was performed at 1100 rpm with an acceleration of 500 for 30 s. Subsequently, it was treated at 110 °C for 2 min and at 150 °C for 3 min. Finally, it was transferred to a vacuum-heated chamber at 260 °C for 1 hour.

## 4. Pattern Polyimide (Top Open Features and Edge)

### 4.1 Deposition of Photoresist

*Materials:* P4620 photoresist

*Equipment:* Spin coater, Hot plate

1. Degas the photoresist for >1 hour prior to spinning (open the bottle and set it in the hood with the lights off).
2. Coat 2 dummy wafers in the spin coater before coating real wafers.
   - *Note: This step saturates the machine with photoresist and changes the atmosphere in the spinner, leading to more consistent photoresist thicknesses between wafers. The remaining steps (4.1.3 through 4.1.5) are performed one wafer at a time; repeat the following procedure once for each wafer. Blow the wafer with N₂ to remove any particles on the surface.*
3. Spin the photoresist to a thickness of 20-22 µm using the following recipe:
   - **First layer:** 5 s, 500 rpm, acceleration 100 rpm/s to spread out the PR puddle, then 2000 rpm at 110 °C for 85 seconds.
   - **Second layer:** 5 s, 500 rpm, acceleration 100 rpm/s to spread out the PR puddle, then 2000 rpm at 110 °C for 180 seconds.
   - This will create a resist mask of approximately 20 µm.
4. If the photoresist is not applied correctly (e.g., if not enough photoresist is used to cover the entire wafer or a particle is stuck on the surface), remove the photoresist and return to step 4.1.

### 4.3 Expose Photoresist

*Equipment:* Hot plate and Mask aligner (MAB6)

Etch mask

1. Load the metal mask into the mask aligner.
   - *Note: All steps (4.3.2 through 4.3.4) are performed one wafer at a time; repeat the following procedure once for each wafer.*
2. Load the wafer into the mask aligner and align the metal layer to the mask pattern.
3. Expose the wafer through etch mask 1 in soft contact mode at 1600 mJ/cm².
4. Place the wafer immediately into a DI water bath after exposure for at least 2 minutes to prevent overheating.

### 4.4 Develop Photoresist

*Materials:* AZ400K developer

*Equipment:* Plastic trays: general use (unlabeled) and designated for developer

*Note: All steps (4.4.1 through 4.4.5) are performed one wafer at a time; repeat the following procedure once for each wafer.*

1. Develop wafer in developer bath (1:4 ratio of AZ400K developer to DI water) for 75 seconds with mild agitation.
   - Development time will need to be adjusted based on the age of the photoresist and developer and environmental conditions.
2. After development, move the wafer quickly to a water bath, then flush 3x with DI water.
3. Blow dry with N₂.
4. Inspect developed features under a microscope and develop for additional time if needed.
5. If the photoresist is not applied correctly (e.g. if the exposure dose is incorrect, if it has been overdeveloped, or if it has been scratched), remove the photoresist and return to step 4.4.1.

### 4.5 Etch Polyimide

1. Etch through the thickness of the top Polyimide layer (down to the metal layer for any exposed metal features) on each wafer using the DRIE.

### 4.6 Remove the Remaining Photoresist

1. Clean off the excess photoresist with acetone.

## 5. Polyimide Stripping from Wafers

1. The polyimide treated in the above steps is soaked in the copper etchant and immersed overnight, allowing the sacrificial layer Cu to completely dissolve. Subsequently, the polyimide is peeled off from the silicon wafer.

## 6. Conductive Connection

1. The sensor is attached to commercial wires using a commercial silver paste.

## 7. Parylene Encapsulation

*Materials:* Parylene dimer

*Equipment:* Parylene PVD

1. Label the backside of each wafer using a permanent marker with the wafer number, date, and which shelf it will be loaded on.
2. Deposit 20 µm of Parylene C on the desired number of wafers.

## Appendices

### A. Polyimide Etching Procedure (DRIE)

*Equipment:* RIE

1. Etch wafers in the RIE through the patterned photoresist using the following parameters:
   - 150 mT, 150 W, 50 sccm O₂.
   - Multiple wafers can be etched at one time (if the chamber is large enough).
   - Perform in two or more steps of 15 minutes or less.
2. After each step, inspect wafers for any remaining polyimide in the etched areas and continue etching as needed.
   - The etch rate varies depending on the equipment used and number of wafers loaded in the machine but should be on the order of 0.15-0.20 µm/minute.
3. If no photoresist remains, stop etching and remove the photoresist via the procedure in Appendix B.

### B. Photoresist Stripping Procedure

*Materials:* Acetone and IPA

*Equipment:* Plastic trays

1. Soak the wafer in an acetone bath for 30-60 seconds with mild agitation to remove the majority of the photoresist.
2. Transfer the wafer to a second acetone bath and soak for >3 minutes with periodic mild agitation.
3. Move the wafer to an IPA bath and soak for >3 minutes with periodic mild agitation.
4. Transfer the wafer to a water bath and soak for >1 minute with periodic mild agitation.
   - Watch out for devices lifting off the wafer at this stage and skip the next step if it will result in the loss of devices.
5. Gently rinse with water and blow dry with N₂.

### C. Material Sources

*Note: Standard materials (e.g. acetone, DI water, cleanroom wipes, etc.) are not listed.*

| Material | Supplier |
|---|---|
| CR-7 Copper etchant | Transene, Danvers, MA |
| Polyimide 2545 | Specialty Coating Systems, Indianapolis, IN |
| P4620 photoresist | AZ Electronic Materials, Branchburg, NJ |
| Parylene dimer | Specialty Coating Systems, Indianapolis, IN |
| AZ400K developer | AZ Electronic Materials, Branchburg, NJ |
| AZ nLOF 2035 | AZ Electronic Materials, Branchburg, NJ |
| AZ917MIF | AZ Electronic Materials, Branchburg, NJ |
| Titanium | Provided by USC Cleanroom |
| Platinum | Provided by USC Cleanroom |

### D. Equipment Models

*Note: Standard equipment (e.g. tweezers, microscopes, N₂ gun, scale, etc.) are not listed.*

| Equipment | Model # | Supplier |
|---|---|---|
| Vacuum oven with N₂ | TVO-2 | Cascade Tek Inc., Longmont, CO |
| Vacuum oven with N₂ | VO914A | Lindberg/Blue M, New Columbia, PA |
| Profilometer | DektakXT | Bruker, Billerica, MA |
| Spin coater | WS-400B-6NPP Lite | Laurell Technologies, North Wales, PA |
| Hot plate | PMC 730 Dataplate | Barnstead/Thermolyne, Dubuque, IA |
| Hot plate | 1000-1 | Electronic Micro Systems, Sutton Coldfield, UK |
| Sonicating bath | 3510 | Branson Ultrasonics, Danbury, CT |
| DRIE | Plasmalab 100 | Oxford Instruments, Bristol, UK |
| RIE | PlasmaPro 80 | Oxford Instruments, Bristol, UK |
| RIE | Series 85 | Technics, Pleasanton, CA |
| Asher | CV200RFS | Yield Engineering Systems, Fremont, CA |
| Mask aligner | MAB6 | OAI, San Jose, CA |
| E-beam evaporator | Mark 40 | CHA Industries, Livermore, CA |
| Sputter | PRO Line PVD 75 | Kurt J. Lesker, Jefferson Hills, PA |
| Parylene PVD | PDS 2010 Labcoter | Specialty Coating Systems, Indianapolis, IN |

### E. References

1. Compliant 3D frameworks instrumented with strain sensors for characterization of millimeter-scale engineered muscle tissues, *Proceedings of the National Academy of Sciences*, 118, e2100077118, 2021.
2. Plasma removal of Parylene C, *J. Micromechanics Microengineering*, 18, 4, p.045004, 2008.

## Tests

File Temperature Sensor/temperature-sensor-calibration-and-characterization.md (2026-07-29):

# Temperature Sensor Calibration and Characterization

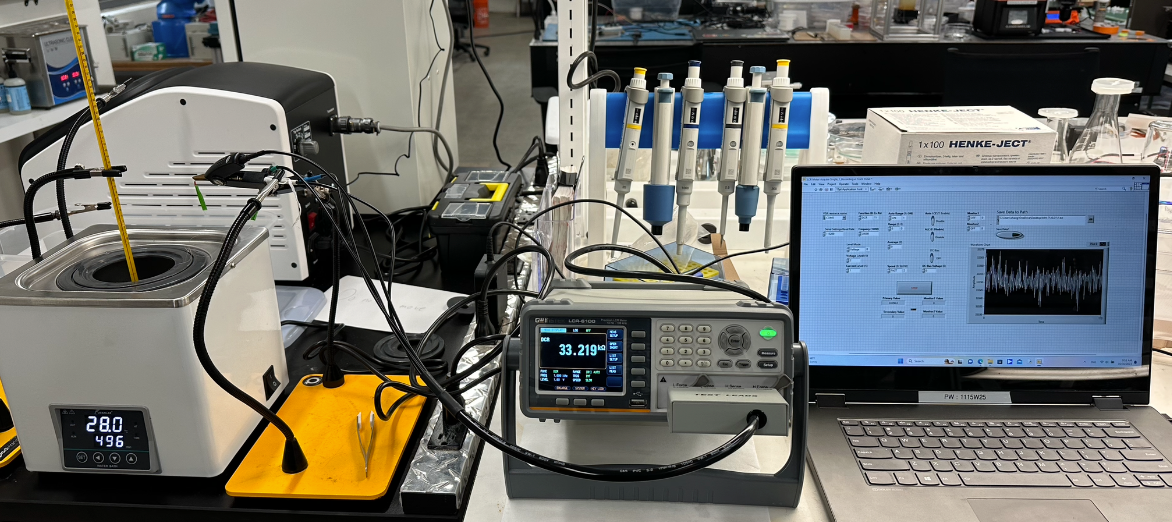
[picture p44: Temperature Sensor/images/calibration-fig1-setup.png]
The setup of temperature sensor calibration and characterization: a heated water bath, LCR meter reading resistance, and a laptop logging data


*The setup of temperature sensor calibration and characterization*

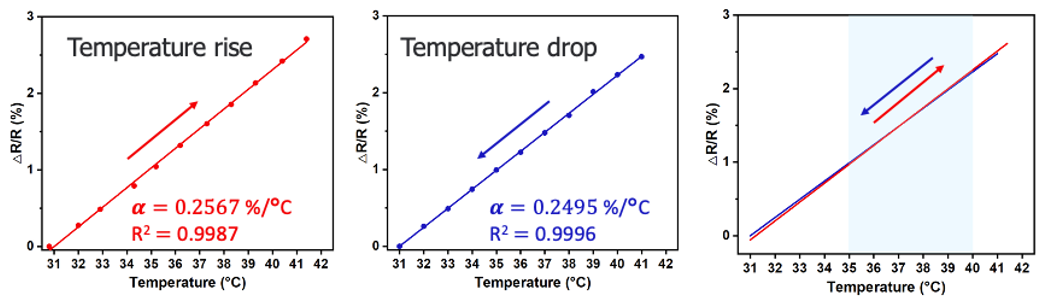
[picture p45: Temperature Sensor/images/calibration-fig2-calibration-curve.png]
Calibration curves of temperature sensor resistance change versus temperature change, showing temperature rise (α = 0.2567 %/°C, R² = 0.9987), temperature drop (α = 0.2495 %/°C, R² = 0.9996), and the combined hysteresis loop


*Calibration curve of temperature sensor resistance change versus temperature change*

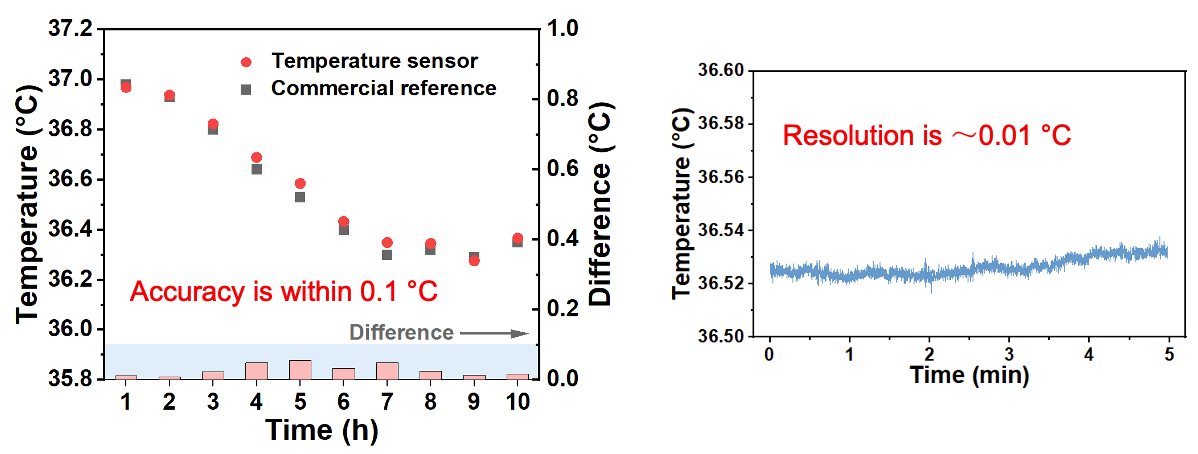
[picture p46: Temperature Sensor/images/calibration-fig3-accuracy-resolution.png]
Accuracy and resolution test of the temperature sensor after calibration: comparison against a commercial reference sensor over 10 hours (accuracy within 0.1 °C), and short-term resolution test (~0.01 °C)


*The accuracy and resolution test of the temperature sensor after calibration*

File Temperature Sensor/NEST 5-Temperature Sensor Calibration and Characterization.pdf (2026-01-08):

## Temperature Sensor Calibration and Characterization

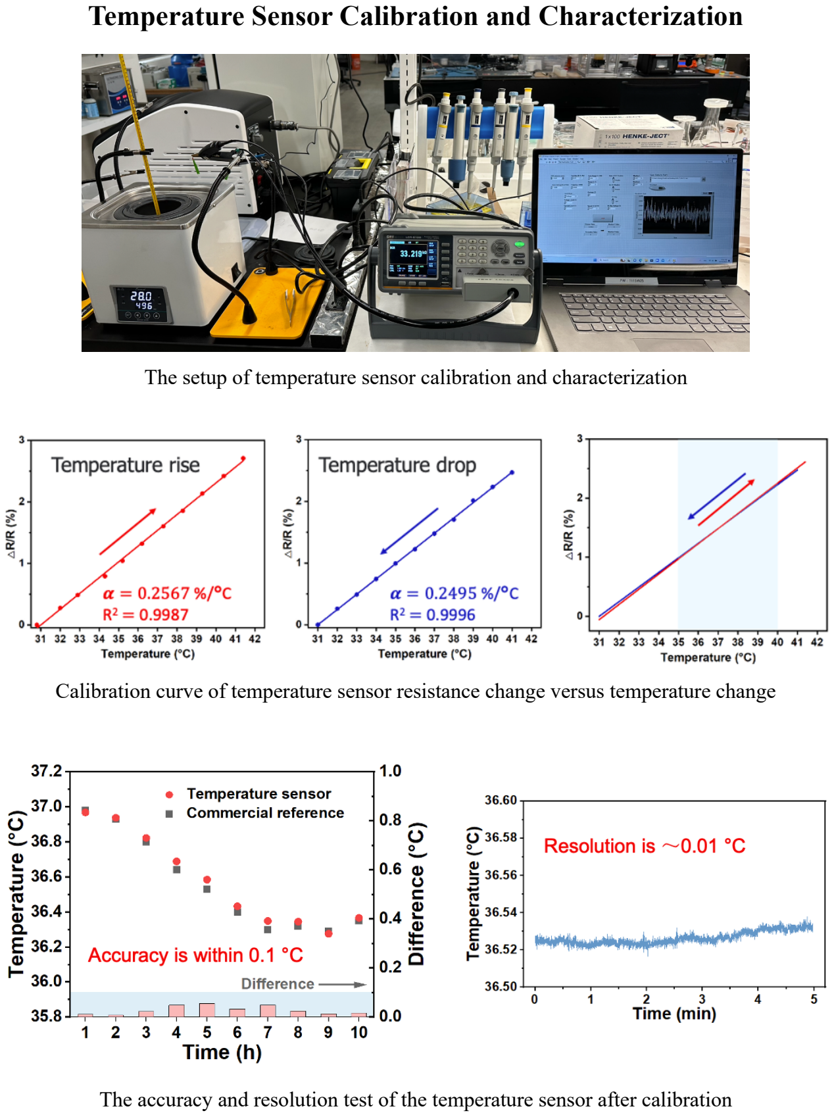
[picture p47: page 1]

The setup of temperature sensor calibration and characterization

Calibration curve of temperature sensor resistance change versus temperature change

The accuracy and resolution test of the temperature sensor after calibration

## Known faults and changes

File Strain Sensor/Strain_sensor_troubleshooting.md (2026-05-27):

# Strain Sensor Troubleshooting Guide

## Pre-strain of sensor
For organs such as the bladder or colon, pre-strain of the sensor is crucial for proper operation. Without applying a pre-strain appropriate for the target organ a user will experience a "dead zone" where the sensor will fold or bend instead of stretching and relaxing, with no change in sensor capacitance. Appropriate pre-strain levels were seen as 15% for use on the colon.



## Sensor size
Even for large animal organs (e.g. sheep bladder), a smaller sensor may be necessary in order to reduce surgical incision sizes. In addition, if a sensor is used with the CapSense board attached, work with the surgeon to ensure that there is sufficient space to place both the sensor and board.



## Wire fragility
Small wires connecting the sensor with implanted or external electronics can be very fragile and break off during surgery. Ensure that any wires are robust enough to handle rough surgical placement. One recommendation is to always place wires inside of a TPU tube that is infilled with silicone.



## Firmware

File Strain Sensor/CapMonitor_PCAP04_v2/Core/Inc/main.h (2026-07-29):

/* USER CODE BEGIN Header */
/**
  ******************************************************************************
  * @file           : main.h
  * @brief          : Header for main.c file.
  *                   This file contains the common defines of the application.
  ******************************************************************************
  * @attention
  *
  * Copyright (c) 2025 STMicroelectronics.
  * All rights reserved.
  *
  * This software is licensed under terms that can be found in the LICENSE file
  * in the root directory of this software component.
  * If no LICENSE file comes with this software, it is provided AS-IS.
  *
  ******************************************************************************
  */
/* USER CODE END Header */

/* Define to prevent recursive inclusion -------------------------------------*/
#ifndef __MAIN_H
#define __MAIN_H

#ifdef __cplusplus
extern "C" {
#endif

/* Includes ------------------------------------------------------------------*/
#include "stm32l4xx_hal.h"

/* Private includes ----------------------------------------------------------*/
/* USER CODE BEGIN Includes */

/* USER CODE END Includes */

/* Exported types ------------------------------------------------------------*/
/* USER CODE BEGIN ET */

/* USER CODE END ET */

/* Exported constants --------------------------------------------------------*/
/* USER CODE BEGIN EC */

/* USER CODE END EC */

/* Exported macro ------------------------------------------------------------*/
/* USER CODE BEGIN EM */

/* USER CODE END EM */

/* Exported functions prototypes ---------------------------------------------*/
void Error_Handler(void);

/* USER CODE BEGIN EFP */

/* USER CODE END EFP */

/* Private defines -----------------------------------------------------------*/
#define B1_Pin GPIO_PIN_13
#define B1_GPIO_Port GPIOC
#define LD2_Pin GPIO_PIN_5
#define LD2_GPIO_Port GPIOA
#define TMS_Pin GPIO_PIN_13
#define TMS_GPIO_Port GPIOA
#define TCK_Pin GPIO_PIN_14
#define TCK_GPIO_Port GPIOA
#define INTN_PG5_Pin GPIO_PIN_10
#define INTN_PG5_GPIO_Port GPIOC
#define SWO_Pin GPIO_PIN_3
#define SWO_GPIO_Port GPIOB

/* USER CODE BEGIN Private defines */

/* USER CODE END Private defines */

#ifdef __cplusplus
}
#endif

#endif /* __MAIN_H */

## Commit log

2026-01-02 Add files via upload
    This is the updated sensor mask designed to integrate with the CapSense PCB board
    [2cm parallel plate sensor for sheep study 2.dwg]
2026-01-02 Add files via upload
    This is the STM32 code for reading the capacitance data from the CapSense PCB board.
